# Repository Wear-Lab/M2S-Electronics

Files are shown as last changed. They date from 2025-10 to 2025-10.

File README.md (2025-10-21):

# M2S-Electronics
Electronics for the M2S Armband

## Details

This are the EAGLE files used to manufacture the four channel amplifier board
for the M2S Armband.

## JLCPCB manufacturing files

Files used to manufacture the PCB, including Gerber files, BOM, and PnP are
located in the JLCPCB folder.

## 2.5mm TRS Connectors

This board uses 2.5mm Right Angle TRS Connectors, commonly used with audio, 
for receiving analog signals. An example part compatible with this board is the
[SJ1-2503A by Same Sky](https://www.digikey.com/en/products/detail/same-sky-formerly-cui-devices/SJ1-2503A/738680)

## I2C Addresses

This board should have its I2C address set prior to use. To do this, short
one of the jumpers located near the STEMMA QT connectors to select an I2C
Address.

Up to four devices can be hooked up to the same I2C bus.

## I2C Fast Mode

To utilize the full potential of this board, make sure that I2C Fast Mode is
enabled. This ensures that the analog signals are recorded at its designed
maximum speed.

## Electrodes

Electrodes used in the M2S project are based on [DFRobot Gravity Analog EMG
Sensor by OYMotion](https://www.dfrobot.com/product-1661.html).
Eight of these Electrodes are used in the project.

[Wiki page](https://wiki.dfrobot.com/analog_emg_sensor_by_oymotion_sku_sen0240)

## License

This project is licensed under CC BY-NC-SA 4.0. To view a copy of this license,
visit https://creativecommons.org/licenses/by-nc-sa/4.0/

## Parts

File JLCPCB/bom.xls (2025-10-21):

Comment | Designator | Footprint | JLCPCB Part #
INA333AIDGKT | U1,U3,U4,U5 | SOP65P490X110-8N | C2057648
SM05B-SRSS-TB(LF)(SN) | J6 | SM05B-SRSS-TB(LF)(SN) | C136657
1.0uF | C3,C11,C17,C23 | 402 | C52923
0.22uF | C1,C2,C9,C10,C15,C16,C21,C22 | 402 | C16772
ADS1015IDGST | U7 | SOP50P490X110-10N | C193969
1KOHM-0402-1/16W-1% | R1,R2,R3,R4,R7,R8,R9,R10,R13,R14,R15,R16,R19,R20,R21,R22 | 402 | C11702
SM04B-SRSS-TB(LF)(SN) | J5 | SM04B-SRSS-TB(LF)(SN) | C160404
LMV324 | U2 | SO14 | C395458
0.1uF | C4,C5,C6,C7,C8,C12,C13,C14,C18,C19,C20,C24,C25,C26,C27,C28,C29,C30 | 402 | C1525
10k | R29,R30,R31 | 402 | C25744
2.0K | R5,R6,R11,R12,R17,R18,R23,R24 | 402 | C4109
REF2033AIDDCT | U6 | SOT95P280X110-5N | C181409

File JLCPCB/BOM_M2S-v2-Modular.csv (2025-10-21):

Comment | Designator | Footprint
0.1uF | C4 | 402
 | C5 | 402
 | C6 | 402
 | C7 | 402
 | C8 | 402
 | C12 | 402
 | C13 | 402
 | C14 | 402
 | C18 | 402
 | C19 | 402
 | C20 | 402
 | C24 | 402
 | C25 | 402
 | C26 | 402
 | C27 | 402
 | C28 | 402
 | C29 | 402
 | C30 | 402
0.22uF | C1 | 402
 | C2 | 402
 | C9 | 402
 | C10 | 402
 | C15 | 402
 | C16 | 402
 | C21 | 402
 | C22 | 402
1.0uF | C3 | 402
 | C11 | 402
 | C17 | 402
 | C23 | 402
10k | R29 | 402
 | R30 | 402
 | R31 | 402
1KOHM-0402-1/16W-1% | R1 | 402
 | R2 | 402
 | R3 | 402
 | R4 | 402
 | R7 | 402
 | R8 | 402
 | R9 | 402
 | R10 | 402
 | R13 | 402
 | R14 | 402
 | R15 | 402
 | R16 | 402
 | R19 | 402
 | R20 | 402
 | R21 | 402
 | R22 | 402
2.0K | R5 | 402
 | R6 | 402
 | R11 | 402
 | R12 | 402
 | R17 | 402
 | R18 | 402
 | R23 | 402
 | R24 | 402
ADS1015IDGST | U7 | SOP50P490X110-10N
INA333AIDGKT | U1 | SOP65P490X110-8N
 | U3 | SOP65P490X110-8N
 | U4 | SOP65P490X110-8N
 | U5 | SOP65P490X110-8N
LMV324 | U2 | SO14
REF2033AIDDCT | U6 | SOT95P280X110-5N
SM04B-SRSS-TB(LF)(SN) | J5 | SM04B-SRSS-TB(LF)(SN)
SM05B-SRSS-TB(LF)(SN) | J6 | SM05B-SRSS-TB(LF)(SN)

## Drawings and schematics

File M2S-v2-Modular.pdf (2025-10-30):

V+ 7 | VIN+ 3 | VIN- 2 | REF 5 | RG_2 8 | RG 1 | V- 4
V+ 7 | VIN+ 3 | VIN- 2 | REF 5 | RG_2 8 | RG 1 | V- 4

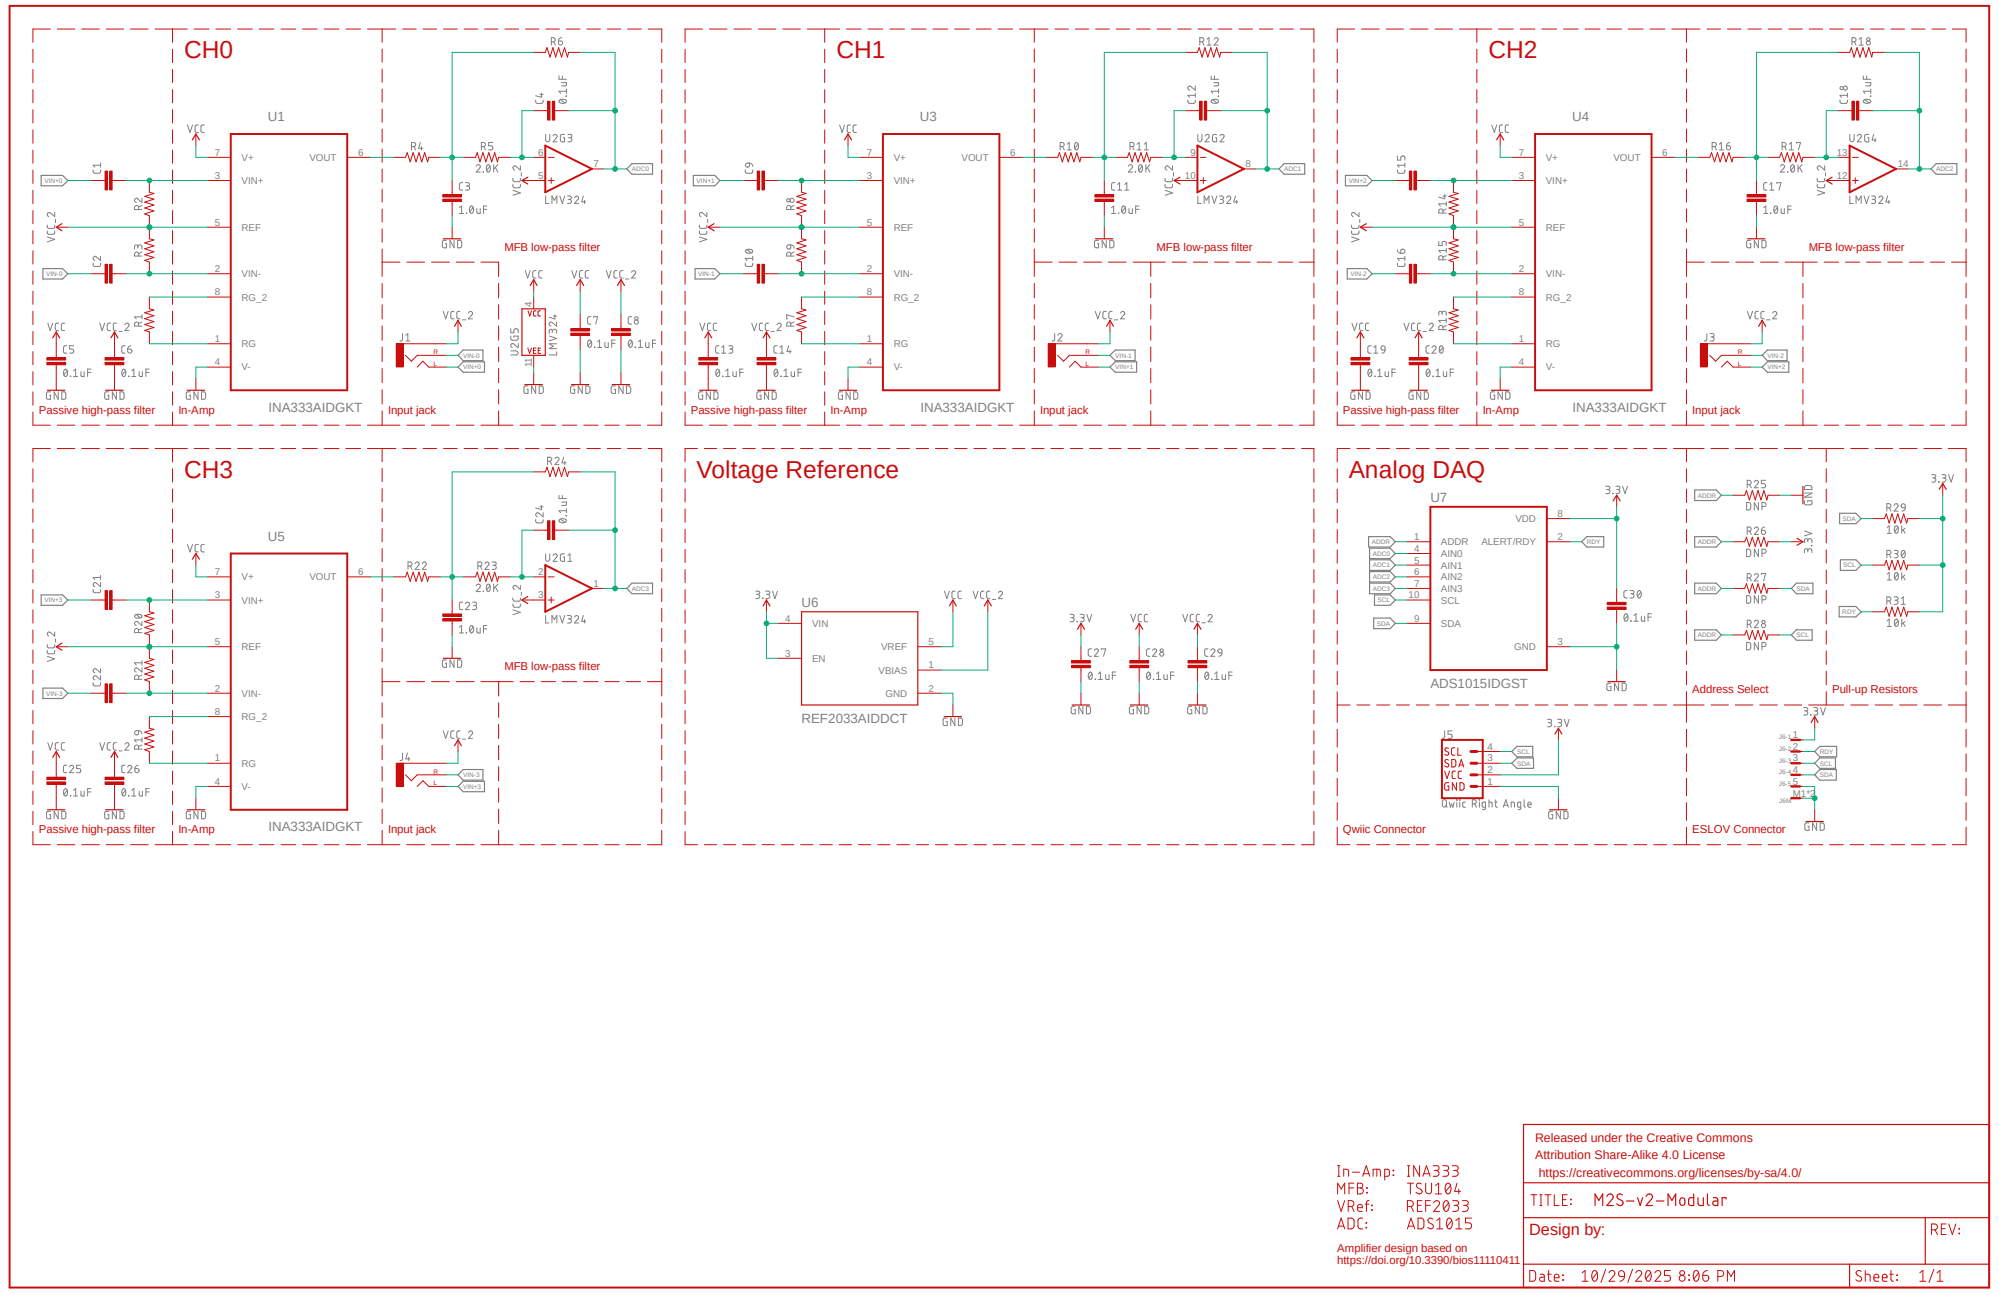
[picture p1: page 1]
INA333AIDGKT; REF2033AIDDCT; ADS1015IDGST; VOUT; VIN+ 3; VIN- 2; REF 5; VREF; 5 GND; 2 VIN 4; VBIAS; ADDR 1; AIN0 4; AIN1 5; AIN2 6; AIN3 7; SCL 10; SDA 9; VDD; 8 ALERT/RDY; 2 GND; VIN+0; VIN+0 VIN-0; VIN-0; ADC0; VIN+1; VIN+1 VIN-1; VIN-1; ADC1; VIN+2; VIN+2 VIN-2; VIN-2; ADC2; ADC2 VIN+3; VIN+3 VIN-3; VIN-3; ADC3; ADC3 ADDR; ADDR; SCL; SCL SCL; SCL SDA; SDA; RDY; RDY RDY; Passive high-pass filter; In-Amp; Input jack; Voltage Reference; Analog DAQ; Address Select; Qwiic Connector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

MFB low-pass filter

Pull-up Resistors

Released under the Creative Commons
Attribution Share-Alike 4.0 License
https://creativecommons.org/licenses/by-sa/4.0/

Amplifier design based on
https://doi.org/10.3390/bios11110411

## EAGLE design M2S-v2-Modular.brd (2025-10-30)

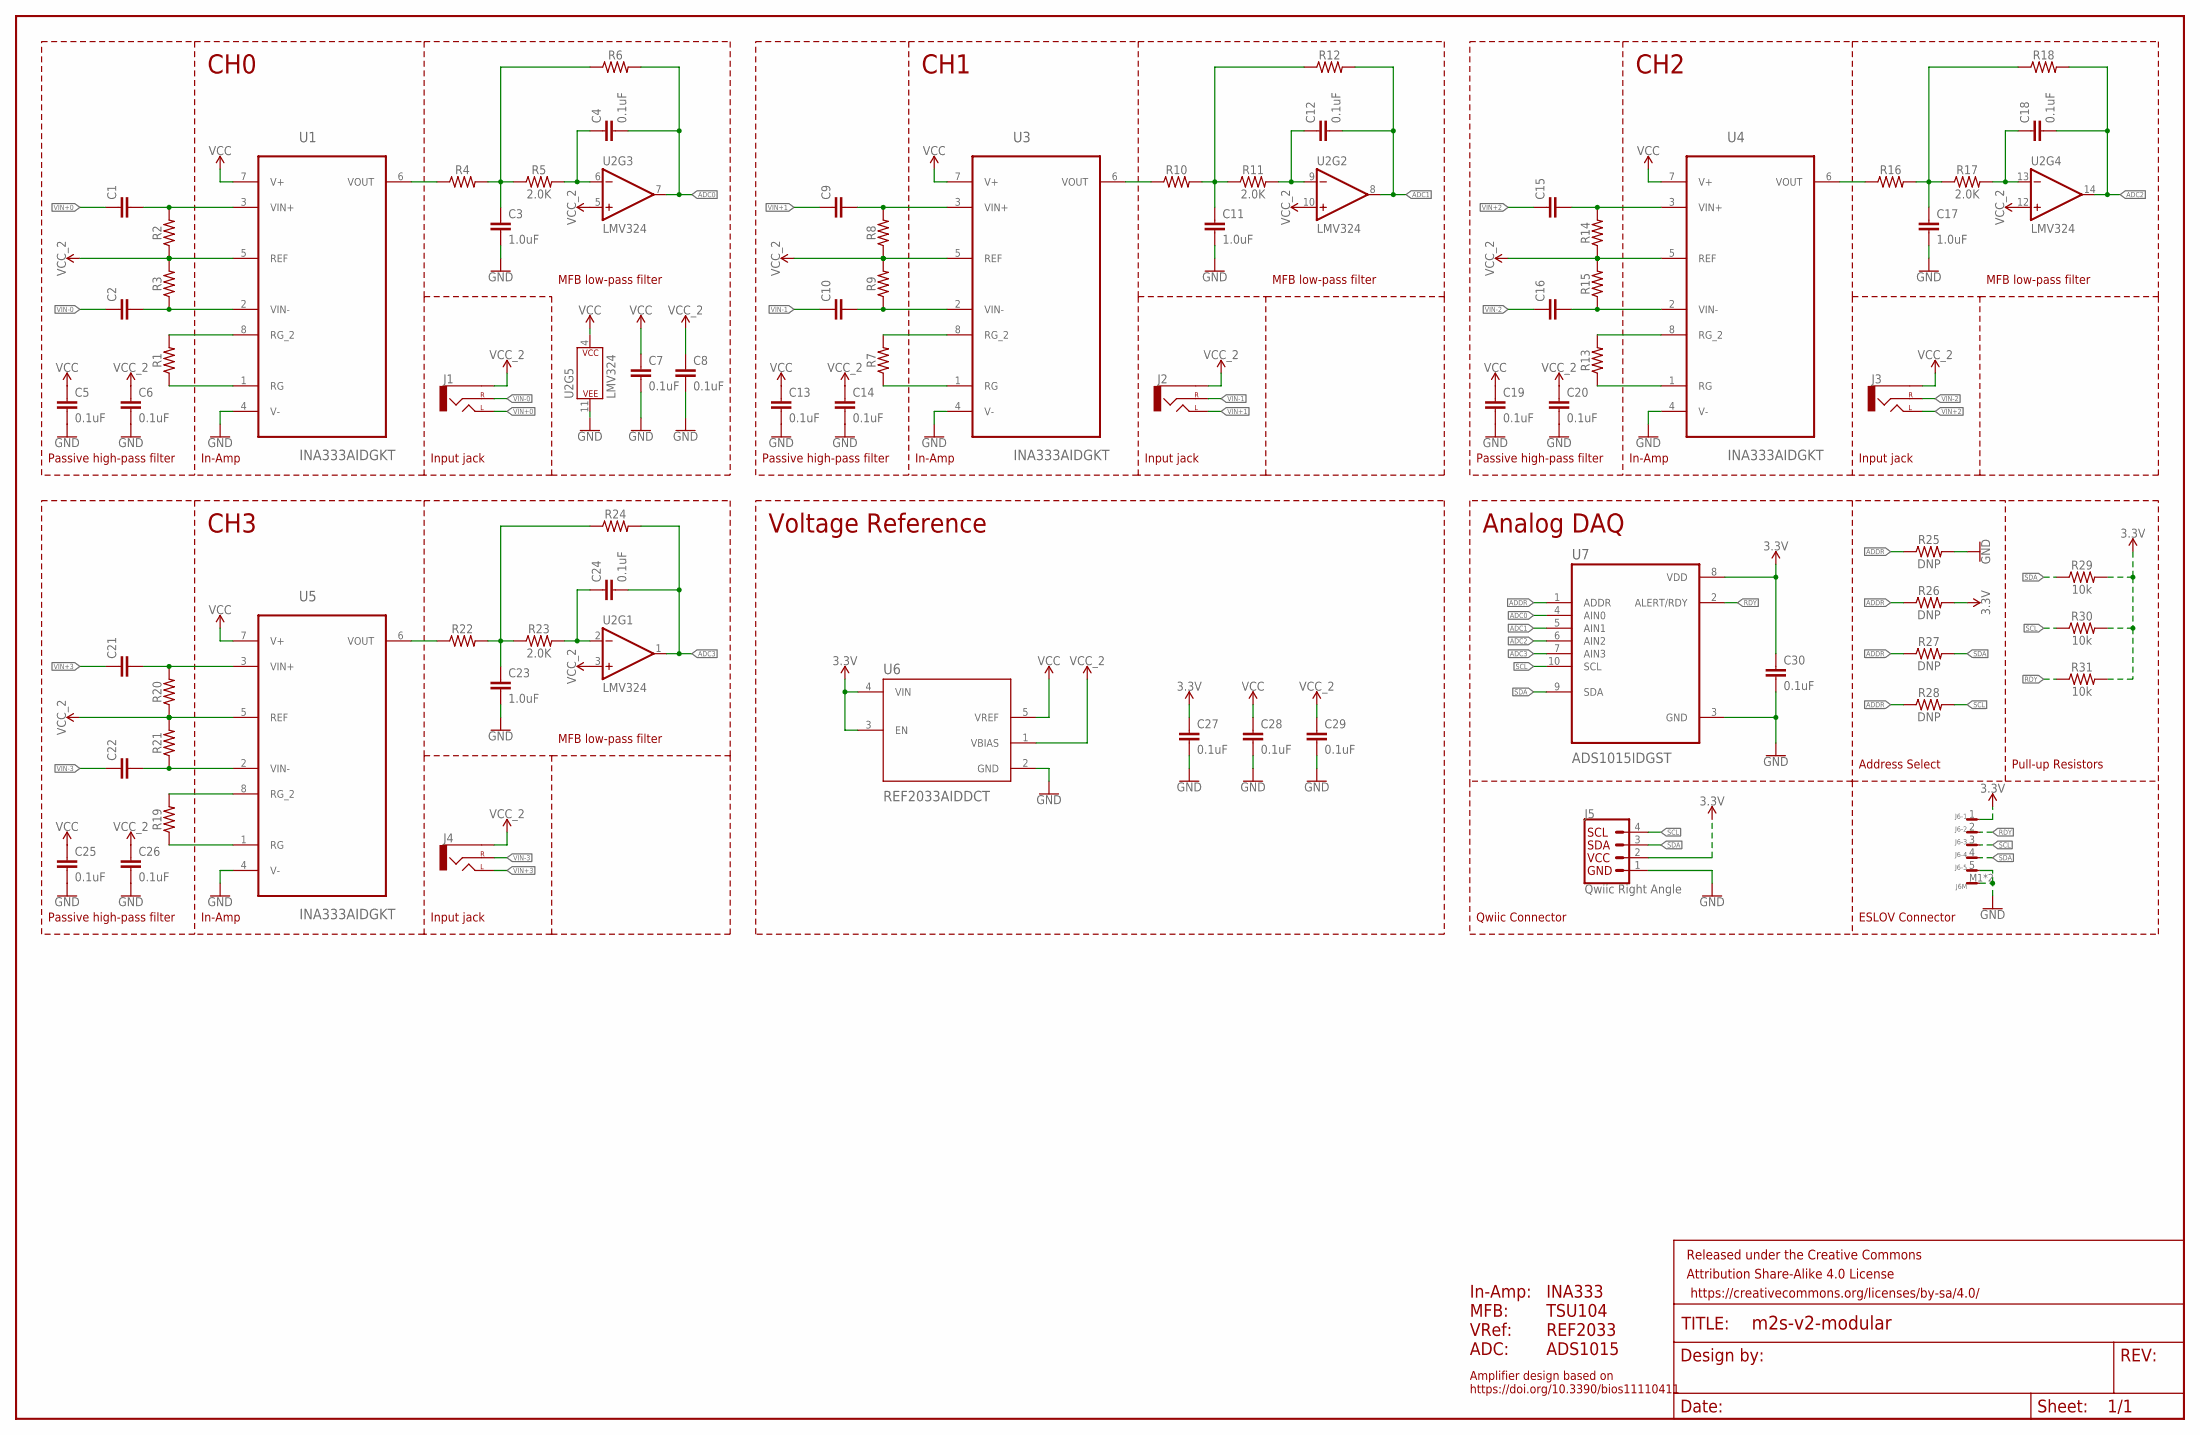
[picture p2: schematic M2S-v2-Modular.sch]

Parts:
C1, C2, C9, C10, C15, C16, C21, C22: 0.22uF; 0402
C3, C11, C17, C23: 1.0uF; 0402
C4, C5, C6, C7, C8, C12, C13, C14, C18, C19, C20, C24, C25, C26, C27, C28, C29, C30: 0.1uF; 0402
FRAME1: FRAME-LEDGERNO_FOOTPRINT; DUMMY
J1, J2, J3, J4: AUDIO_JACK_2.5MM_2.5MM; STEREOJACK2.5MM_STEREOJACK2.5MM
J5: Qwiic Right Angle; JST04_1MM_RA
J6: SM05B-SRSS-TB
R1, R7, R13, R19: 1KOHM-0402-1/16W-1%; 0402
R2, R3, R4, R6, R8, R9, R10, R12, R14, R15, R16, R18, R20, R21, R22, R24: 0402
R5, R11, R17, R23: 2.0K; 0402
R25, R26, R27, R28: DNP; 0402
R29, R30, R31: 10k; 0402
U1, U3, U4, U5: INA333AIDGKT; SOP65P490X110-8N
U2: LMV324; SO14
U6: REF2033AIDDCT; SOT95P280X110-5N
U7: ADS1015IDGST; SOP50P490X110-10N

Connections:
3.3V: C27.1, C30.1, J5.2, J6.1, R26.2, R29.2, R30.2, R31.2, U6.3 (EN), U6.4 (VIN), U7.8 (VDD)
ADC0: C4.2, R6.2, U2.7 (OUT), U7.4 (AIN0)
ADC1: C12.2, R12.2, U2.8 (OUT), U7.5 (AIN1)
ADC2: C18.2, R18.2, U2.14 (OUT), U7.6 (AIN2)
ADC3: C24.2, R24.2, U2.1 (OUT), U7.7 (AIN3)
ADDR: R25.1, R26.1, R27.1, R28.1, U7.1 (ADDR)
GND: C3.2, C5.2, C6.2, C7.2, C8.2, C11.2, C13.2, C14.2, C17.2, C19.2, C20.2, C23.2, C25.2, C26.2, C27.2, C28.2, C29.2, C30.2, J5.1, J6.5, J6.M1, J6.M2, R25.2, U1.4 (V-), U2.11 (P$V-), U3.4 (V-), U4.4 (V-), U5.4 (V-), U6.2 (GND), U7.3 (GND)
unnamed: R1.2, U1.8 (RG_2)
unnamed: R1.1, U1.1 (RG)
unnamed: C1.2, R2.2, U1.3 (VIN+)
unnamed: C2.2, R3.1, U1.2 (VIN-)
unnamed: R4.1, U1.6 (VOUT)
unnamed: C3.1, R4.2, R5.1, R6.1
unnamed: C4.1, R5.2, U2.6 (-IN)
unnamed: R7.2, U3.8 (RG_2)
unnamed: R7.1, U3.1 (RG)
unnamed: C9.2, R8.2, U3.3 (VIN+)
unnamed: C10.2, R9.1, U3.2 (VIN-)
unnamed: R10.1, U3.6 (VOUT)
unnamed: C11.1, R10.2, R11.1, R12.1
unnamed: C12.1, R11.2, U2.9 (-IN)
unnamed: R13.2, U4.8 (RG_2)
unnamed: R13.1, U4.1 (RG)
unnamed: C15.2, R14.2, U4.3 (VIN+)
unnamed: C16.2, R15.1, U4.2 (VIN-)
unnamed: R16.1, U4.6 (VOUT)
unnamed: C17.1, R16.2, R17.1, R18.1
unnamed: C18.1, R17.2, U2.13 (-IN)
unnamed: R19.2, U5.8 (RG_2)
unnamed: R19.1, U5.1 (RG)
unnamed: C21.2, R20.2, U5.3 (VIN+)
unnamed: C22.2, R21.1, U5.2 (VIN-)
unnamed: R22.1, U5.6 (VOUT)
unnamed: C23.1, R22.2, R23.1, R24.1
unnamed: C24.1, R23.2, U2.2 (-IN)
RDY: J6.2, R31.1, U7.2 (ALERT/RDY)
SCL: J5.4, J6.3, R28.2, R30.1, U7.10 (SCL)
SDA: J5.3, J6.4, R27.2, R29.1, U7.9 (SDA)
VCC: C5.1, C7.1, C13.1, C19.1, C25.1, C28.1, U1.7 (V+), U2.4 (P$V+), U3.7 (V+), U4.7 (V+), U5.7 (V+), U6.5 (VREF)
VCC_2: C6.1, C8.1, C14.1, C20.1, C26.1, C29.1, J1.RING1 (SLEEVE), J2.RING1 (SLEEVE), J3.RING1 (SLEEVE), J4.RING1 (SLEEVE), R2.1, R3.2, R8.1, R9.2, R14.1, R15.2, R20.1, R21.2, U1.5 (REF), U2.3 (+IN), U2.5 (+IN), U2.10 (+IN), U2.12 (+IN), U3.5 (REF), U4.5 (REF), U5.5 (REF), U6.1 (VBIAS)
VIN+0: C1.1, J1.SHIELD (LEFT)
VIN+1: C9.1, J2.SHIELD (LEFT)
VIN+2: C15.1, J3.SHIELD (LEFT)
VIN+3: C21.1, J4.SHIELD (LEFT)
VIN-0: C2.1, J1.TIP (RIGHT)
VIN-1: C10.1, J2.TIP (RIGHT)
VIN-2: C16.1, J3.TIP (RIGHT)
VIN-3: C22.1, J4.TIP (RIGHT)

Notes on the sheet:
Passive high-pass filter
In-Amp
Input jack
MFB low-pass filter
CH0
In-Amp: MFB: VRef: ADC:
INA333 TSU104 REF2033 ADS1015
Amplifier design based on https://doi.org/10.3390/bios11110411
CH1
CH2
CH3
Voltage Reference
Analog DAQ
Address Select
Qwiic Connector
ESLOV Connector
Pull-up Resistors

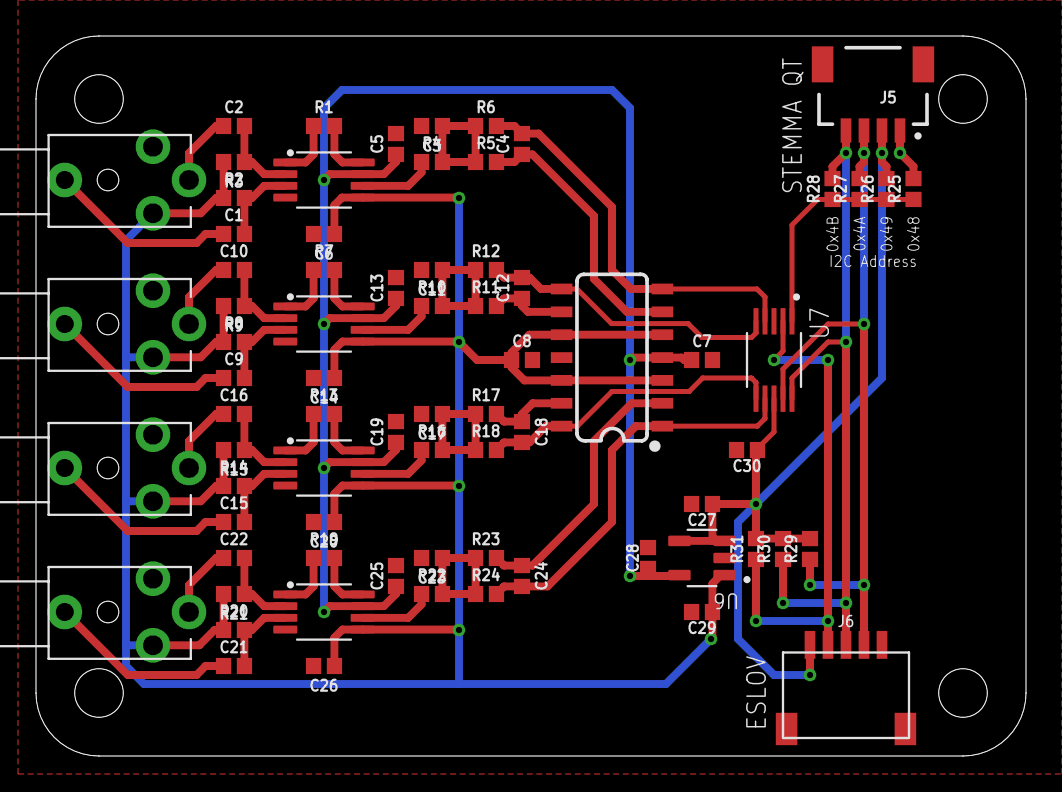
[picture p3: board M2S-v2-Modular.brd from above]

Board: 2 copper layers, 55.0 x 40.0 mm, 75 parts (0 on the bottom side), 48 nets.

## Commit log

2025-10-21 ADC Fix
    Changed ADC from ADS1115 to ADS1015.
    Added EAGLE libraries.
    Updated/Fixed JLCPCB BOM and PnP files.
    Added PDF for the schematics for easier access.
    [BOM_M2S-v2-Modular.csv, M2S-v2-Modular.brd, M2S-v2-Modular.sch, bom.xls]
2025-10-30 Fix ESLOV Pinout
    Fixed ESLOV Pinout, swapped SDA and INT pins.
    [M2S-v2-Modular.brd, M2S-v2-Modular.sch]

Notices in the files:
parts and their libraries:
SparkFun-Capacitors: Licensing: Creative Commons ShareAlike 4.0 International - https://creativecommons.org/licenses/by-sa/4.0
